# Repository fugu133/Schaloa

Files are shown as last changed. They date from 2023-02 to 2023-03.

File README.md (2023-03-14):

# 超小型分光光度計Schaloa
## 概要
浜松ホトニクスのマイクロ分光器[C12880MA](https://www.hamamatsu.com/jp/ja/product/optical-sensors/spectrometers/mini-spectrometer/C12880MA.html)を用いた分光光度計モジュールのハードウェア設計データです．  
本装置を使うと可視領域の分光計測や吸光光度分析がハンディサイズで実現可能です．  
主にCADはEagleとFusionを使用しています．詳しい仕様は[こちら](design_specifications.pdf)    

## 基板のイメージ
### メイン制御基板
分光器や各系の制御，PCとの通信を行います．



### 分光器基板
分光器のブレークアウト基板です．



## 計測デモ
蛍光灯と一般的な白色LEDの放射光スペクトルを計測しました．


### 蛍光灯
405nm，436nm，546nm及び577nm付近に鋭いピークが見られます．  
これらは蛍光灯の発光源である水銀の原子スペクトルと一致しています．  
この光を管内の蛍光体に照射すると蛍光により白色光が作成されます．

### 白色LED
頂点が過剰露出により潰れていますが，440nm付近に鋭いピークが見られます．  
これはパッケージ内部の青色LEDによる光だと考えられます．所謂ブルーライトです．  
また550nm-560nm付近を中心に広いピークを確認できます．  
これは黄色系の蛍光体の蛍光だと考えられます．白色LEDはこのようにして白色光を作成します．

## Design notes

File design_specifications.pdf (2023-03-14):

Kaiji Takeuchi 2019
[SCHLOA version beta]

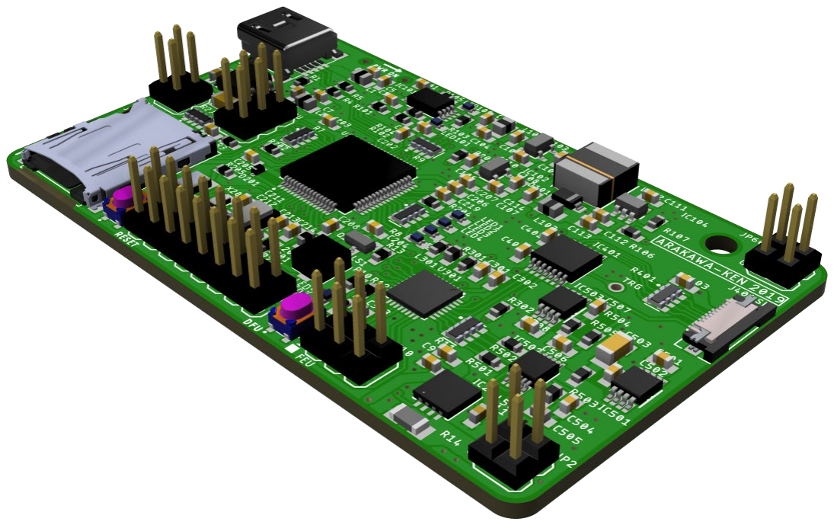
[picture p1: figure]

p. 1

# SCHLOA v1.0.0

Compact Portable Spectrophotometer | Developed by Kaiji Takeuchi 2019
1. 概要

SCHLOA (Fig.1.1) は分光分析法を採用した超小型ポータブル分光光度計です．コア・デ バイスである分光器には Hamamatsu Photonics 製ミニ分光器に対応しています．本システ

ムは持ち運べるサイズながら，反射，吸収，拡散及び散乱光の分光分析に対する，幅広い 応用が可能です．コア・システムには Arm® Mbed™を採用しているため，ファームウェア

開発も容易になります．

2. 特徴
・32 ビット Cortex-M4 コア・プロセッサ：STM32F446RE(180MHz)
・32 ビット Cortex-M4 デジタルフロントエンド・プロセッサ：STM32L432KC(80MHz) ・Arm® Mbed™ Mbed OS5 対応

・対応分光器波長感度
Hamamatsu Photonics MS series
-C11708MA：640nm～1050nm
-C10988MA-01：340nm～750nm
Hamamatsu Photonics micro series -C12880MA：340nm～780nm
-C12666MA：340nm～850nm
・蓄積(露出)時間：～100µs
・ADC キャプチャ・レート：～1MHz

・高精度・高速セトリング アナログフロントエンド
・ADC 専用リファレンス電源内臓
・LED ドライバ内臓
-PWM(電流フィードバック)

・リアルタイムクロック内臓
・各データ転送(記録)方式に対応
-Bluetooth SPP (専用基板が必要)
-USB I/F
-SD Memory Card

Fig. 1.1 SCHLOA Board

p. 2
3. 目次
1. 概要 | 1
2. 特徴 | 1
3. 目次 | 2
4. ブロック図と機能説明 | 5
■ メインボード | 5
5. ピンマップと機能説明 | 6
■ ピンマップ | 6
・Supply Port (JP1) | 6
・MPU Debug Port (JP601) | 6
・FEU Debug Port (JP602) | 6
・External Connection Port (JP603) | 7
・LED Output Port (JP2) | 7
・Spectrometer Connection Port (J401) | 7
・Auxiliary Port (JP604) | 7
■ 機能説明 | 8
6. 絶対定格 | 10
7. 推奨動作範囲 | 10
8. 内部回路とジャンクション | 11
■ 内部回路 | 11
・Main System | 11
・Power Unit | 12
・Main Processing Unit | 13
・Front End Processing Unit | 14
・Spectrometer Unit | 15
・A/D Convert Unit | 16
・Breakeout Pins (External Access Port) | 17
■ 内部ジャンクション | 18
9. 内部回路の動作と機能説明 | 20
■ パワーマルチプレクサの動作 | 20
・電源供給の切り替え | 20
・電流制限 | 20
■ リセット回路の動作 | 21
・パワーオン時のリセットシーケンス | 21
■ LED ドライバの動作 | 22
・出力電流の設定 | 22

p. 3
・輝度調整 | 22
・保護回路の動作 | 22
■ 音声出力機能 | 22
■ 分光器の蓄積 (露出) 動作 | 23
・タイミングチャート | 23
・推奨動作範囲 | 23
・最小蓄積 (露出) 時間の算出法 | 23
■ ビデオ信号のキャプチャ動作 | 24
・トリガ・モード | 24
・タイミングチャート | 25
・AD コンバータのリファレンス電源 | 26
■ メインコントロール・ユニットとデジタルフロントエンド・ユニットの通信 ........ 27
・タイミングチャート | 27
■ データフォーマット | 28
・Check Sum (XOR)の算出法 | 30
ファームウェア書き込みとシリアルデバッグ | 31
・DAP または Writer を使用する場合 | 31
・DFU Bootloader を使用する場合 | 31
10. ソフトウェアの機能説明 | 32
■ システムクロックの設定 | 32
・JSON を変更し HSE XTAL の使用を有効にする | 32
・クロック周辺の設定を自身で行い HSE XTAL の使用を有効にする | 33
■ MCO の設定 | 34
Mbed プラットフォームの変更箇所 | 35
・C++11 でプログラミングを行う | 35
・SPI 関係の API の改良 | 35
■ 専用 API (schloa-api) の概要 | 37
■ ADC API | 37
・ADC Class | 37
■ Backup API | 39
・Backup Class | 39
■ Communication API | 40
・CommunicationMaster Class | 40
・CommunicationSlave Class | 44
・MPUToFEUFitting Class | 47
・FEUToMPUFitting Class | 54

p. 4
・Fitting Class | 56
■ DebugPort API | 58
・DebugPort Class | 58
■ DrawSpectrum API | 59
・DrawSpectrum Class | 59
・DrawSpectrumAnalyze Class | 61
■ FastOut API | 63
・FastOut Class | 63
■ LEDDrive API | 65
・LEDDrive Class | 65
■ LiquidCrystal API | 67
・LiquidCrystal Class | 67
■ SoftPWMOut API | 69
・SoftPWMOut Class | 69
■ SystemTicker API | 72
・System Ticker Class | 72
■ Sound API | 75
・Sound Class | 75
■ Spectoro API | 77
・Spectro Class | 77
■ SwitchStatus API | 80
・SwitchStatus Class | 80
■ スペクトル表示アプリケーション drawSpectrum | 82
・データフォーマット | 83
・操作方法 | 85

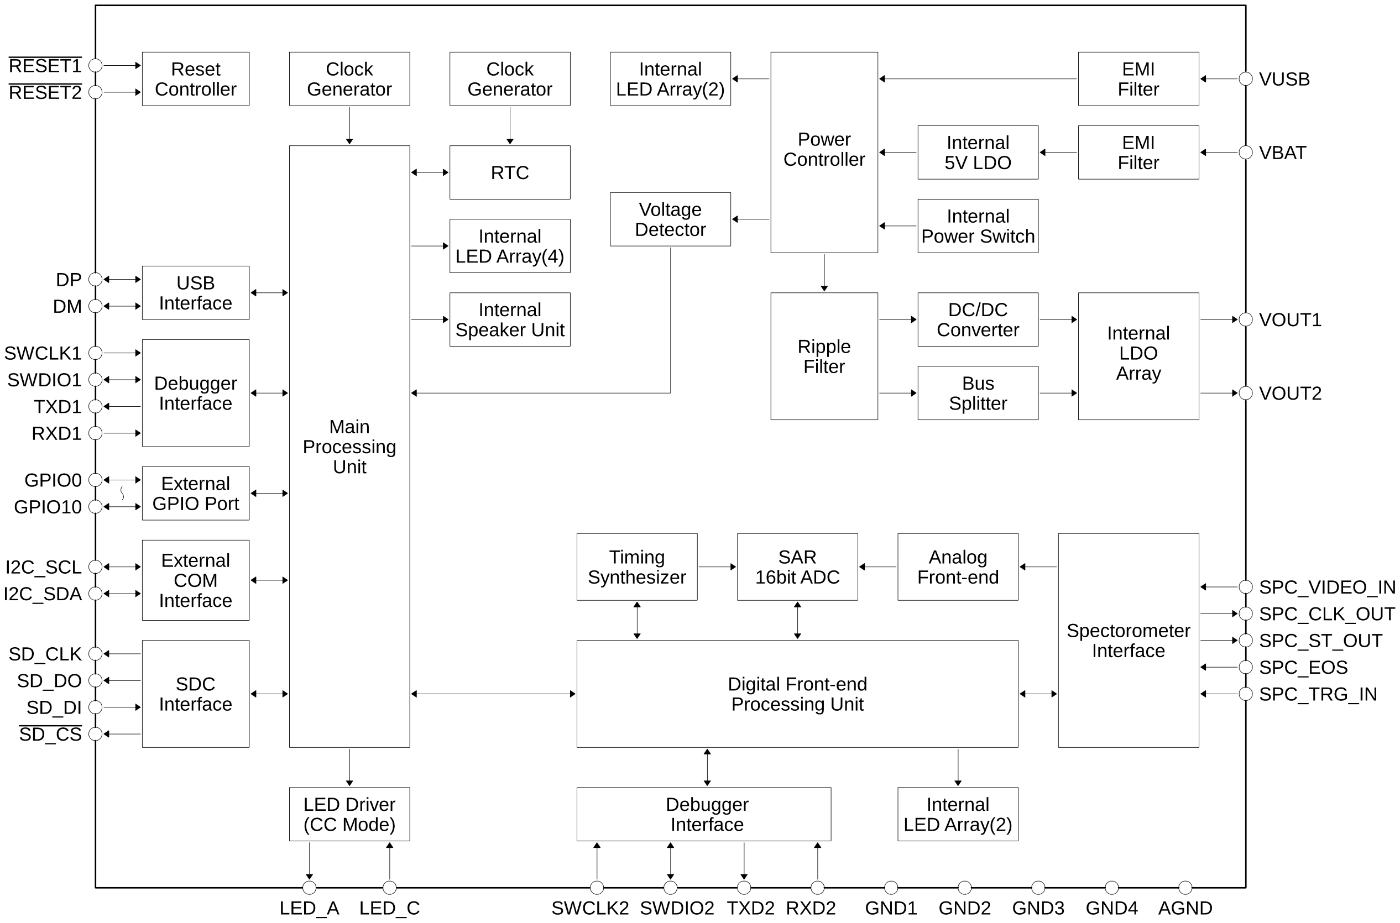
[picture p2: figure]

p. 5
4. ブロック図と機能説明

■ メインボード

Fig. 4.1 Main Board’s System Block Diagram

p. 6
5. ピンマップと機能説明

■ ピンマップ

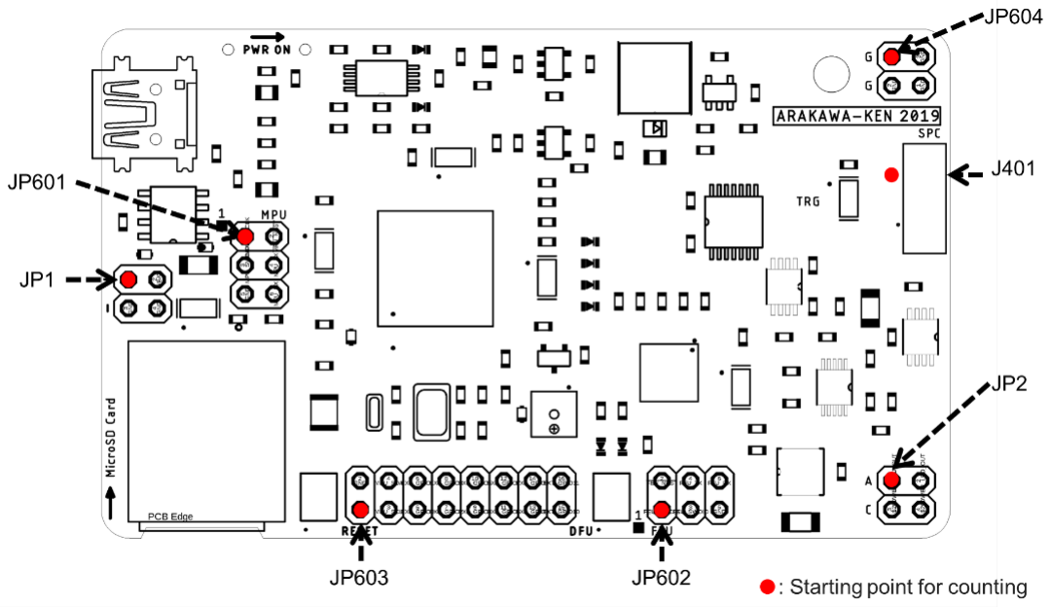
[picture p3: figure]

Fig. 5.1 Junction Ports Map

・Supply Port (JP1)

Fig. 5.2 JP1 Pins Map

・MPU Debug Port (JP601)

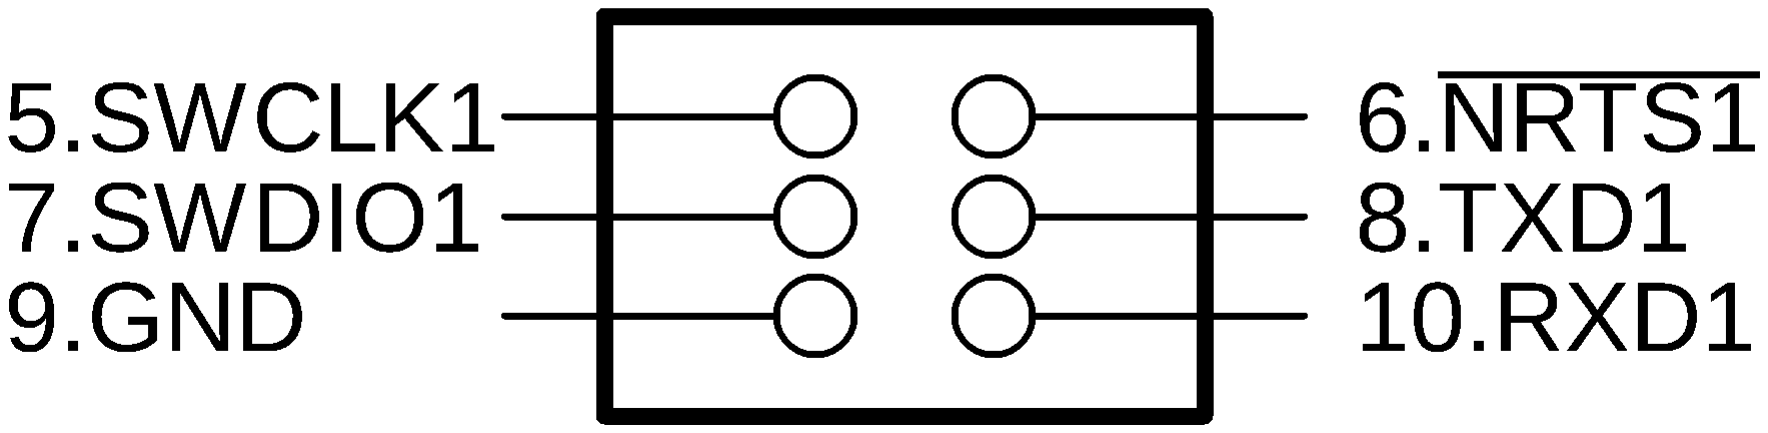
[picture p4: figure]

Fig. 5.3 JP601 Pins Map

・FEU Debug Port (JP602)

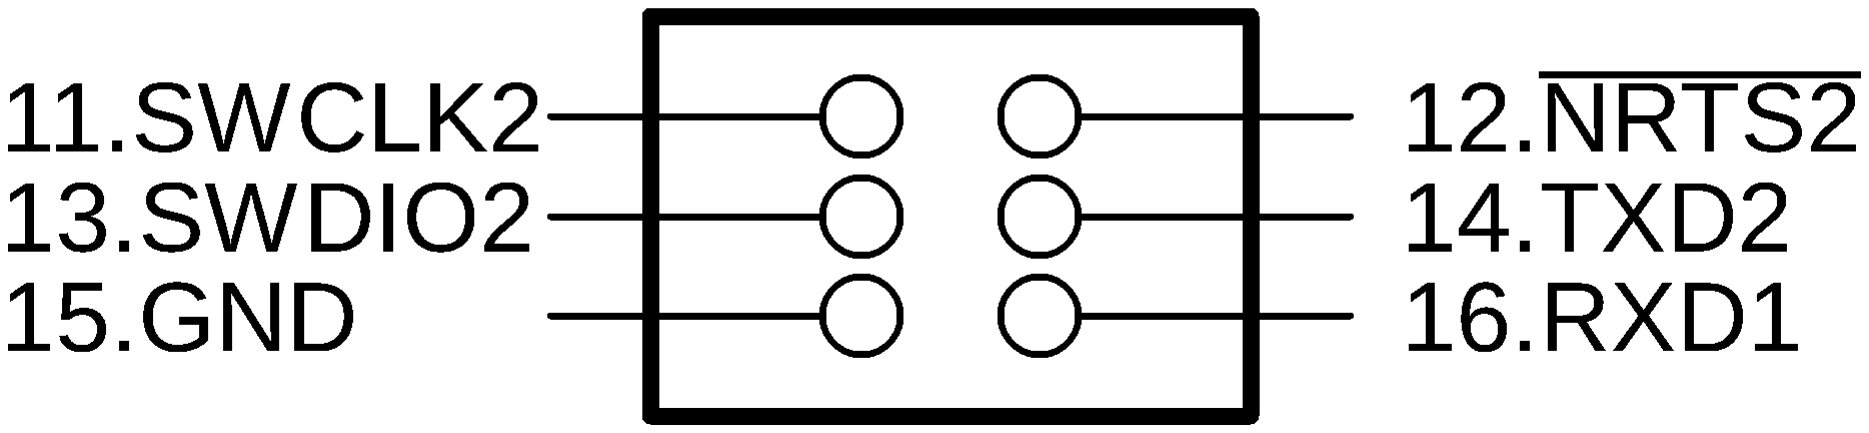
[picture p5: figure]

Fig. 5.4 JP602 Pins Map

p. 7

・External Connection Port (JP603)

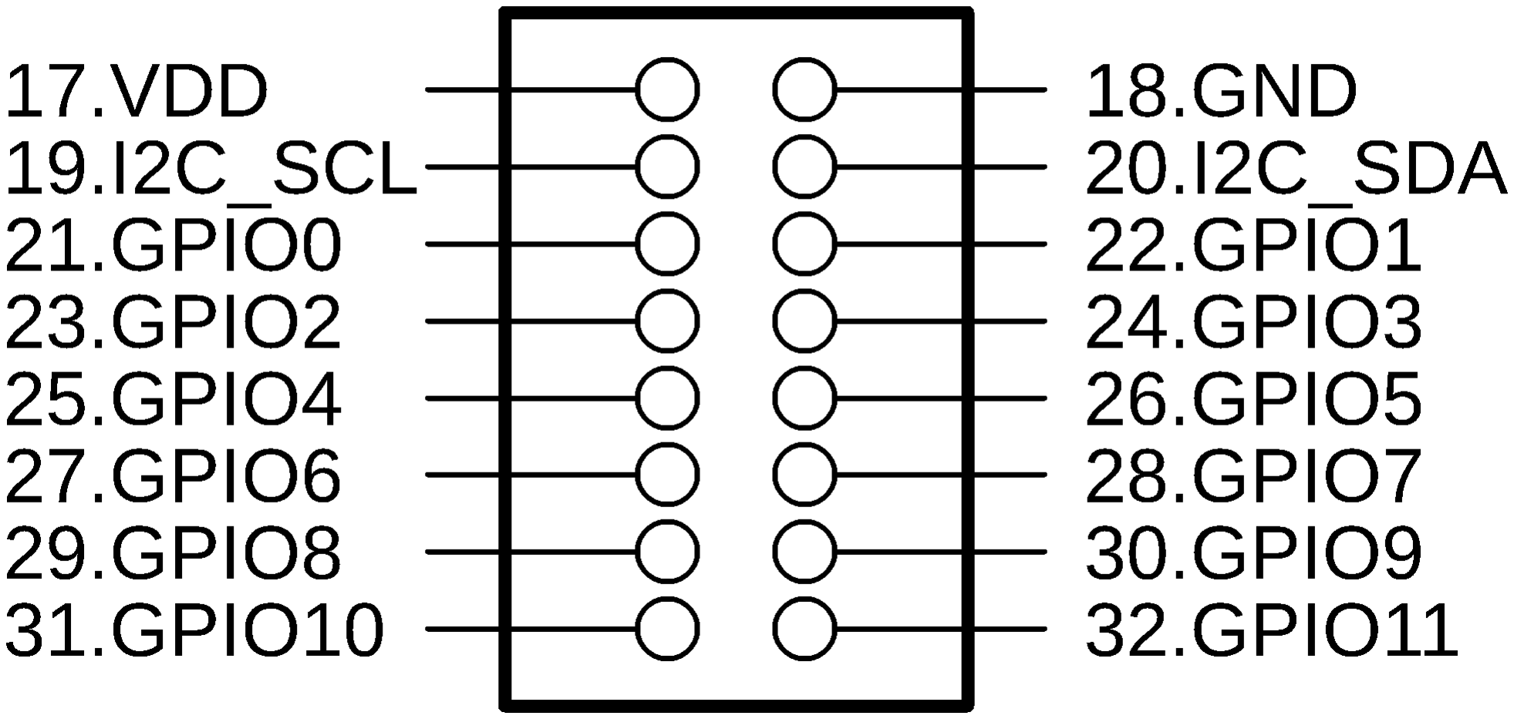
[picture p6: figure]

Fig. 5.5 JP603 Pins Map

・LED Output Port (JP2)

Fig. 5.6 JP2 Pins Map

・Spectrometer Connection Port (J401)

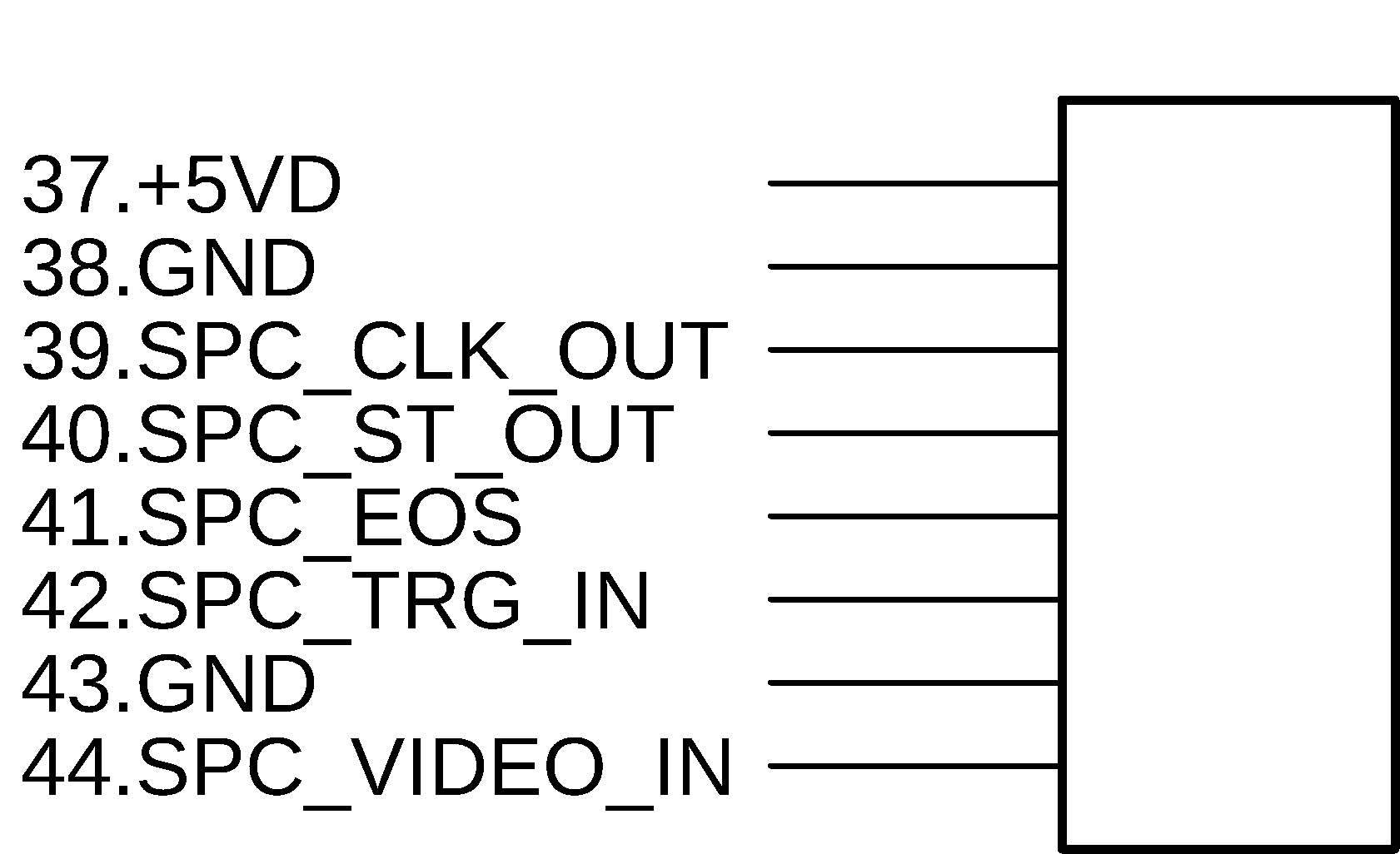
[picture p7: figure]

Fig. 5.7 J401 Pins Map

・Auxiliary Port (JP604)

Fig. 5.8 JP604 Pins Map

p. 8

■ 機能説明
Tabel 5.1 Pin Functions
NO. | Symbol | I/O | Tolerant | Function
1 | VBAT | - | - | Power Supply Pin, 5.1~10V
2 | VBAT | - | - | Power Supply Pin, 5.1~10V
3 | GND | - | - | Ground Pin
4 | GND | - | - | Ground Pin
5 | SWCLK1 | I | FT | MPU JTAG/SWD Clock Input Pin
6 | NRST1 | I | TT | MPU Reset Input Pin, Active Low
7 | SWDIO1 | I/O | FT | MPU JTAG/SWD Data I/O Pin
8 | TXD1 | O | FT | MPU UART Transmit Data Pin -Connect the RXD pin of the debugger.
9 | GND | - | - | Ground Pin
10 | RXD1 | I | FT | MPU UART Receive Data Pin -Connect the RXD pin of the debugger.
11 | SWCLK2 | I | FT | FEU JTAG/SWD Clock Input Pin -Connect the SWCLK pin of the debugger.
12 | NRST2 | I | TT | FEU Reset Input Pin, Active Low -Connect the Reset pin of the debugger.
13 | SWDIO2 | I/O | FT | FEU JTAG/SWD Data I/O Pin -Connect the SWDIO pin of the debugger.
14 | TXD2 | O | FT | FEU UART Transmit Data Pin -Connect the RXD pin of the debugger.
15 | GND | - | - | Ground Pin
16 | RXD2 | I | FT | FEU UART Receive Data Pin -Connect the RXD pin of the debugger
17 | +5VD | - | - | Digital Power Output Pin, +5V Constant
18 | GND | - | - | Ground Pin
19 | I2C_SCL~ | I/O | FT | I-squared-C Slave Clock Pin, Open Drain
20 | I2C_SDA~ | I/O | FT | I-squared-C Slave Data Pin, Open Drain
21 | EXT_GPIO0 | I/O | FT | External General-Purpose Input/Output Pin
22 | EXT_GPIO1 | I/O | FT | External General-Purpose Input/Output Pin -PWM is Available
23 | EXT_GPIO2 | I/O | FT | External General-Purpose Input/Output Pin -PWM is Available.

p. 9

Note1 : FT = 5V Input Tolerant，TT = 3.3V Input Tolerant.
Note2 : チルダ表記(~)された入出力ピンはオープン・ドレインです．
Note3 : アスタリスク表記(*)された入出力ピンは内部でプル・ダウンされています．
24 | EXT_GPIO3 | I/O | FT | External General-Purpose Input/Output Pin -PWM is Available.
25 | EXT_GPIO4 | I/O | FT | External General-Purpose Input/Output Pin -PWM is Available.
26 | EXT_GPIO5 | I/O | FT | External General-Purpose Input/Output Pin -PWM is Available.
27 | EXT_GPIO6 | I/O | FT | External General-Purpose Input/Output Pin
28 | EXT_GPIO7 | I/O | FT | External General-Purpose Input/Output Pin
29 | EXT_GPIO8 | I/O | FT | External General-Purpose Input/Output Pin
30 | EXT_GPIO9 | I/O | FT | External General-Purpose Input/Output Pin
31 | EXT_GPIO10 | I/O | FT | External General-Purpose Input/Output Pin
32 | EXT_GPIO11 | I/O | FT | External General-Purpose Input/Output Pin
33 | LED_A | O | - | Power LED Anode Pin, MAX 500mA
34 | LED_A | O | - | Power LED Anode Pin, MAX 500mA
35 | LED_C | I | - | Power LED Cathode Pin, Current FB
36 | LED_C | I | - | Power LED Cathode Pin, Current FB
37 | +5VD | - | - | Digital Power Output Pin, +5V Constant
38 | GND | - | - | Ground Pin
39 | SPC_CLK_OUT* | O | FT | Spectrometer Clock Output Pin -Mounting R502, Auto Trigger Mode. -Mounting R501, Manual Trigger Mode.
40 | SPC_ST_OUT* | O | FT | Spectrometer Start Pulse Output Pin
41 | SPC_EOS* | I | FT | Spectrometer End of Scan Detect Pin
42 | SPC_TRG_IN* | I | FT | Spectrometer Trigger Pulse Input Pin - No connection with controller
43 | GND | - | - | Ground Pin
44 | SPC_VIDEO_IN | I | - | Spectrometer Video Signal Input, 0~+5V
45 | GND | - | - | Ground Pin
46 | GND | - | - | Ground Pin
47 | GND | - | - | Ground Pin
48 | GND | - | - | Ground Pin

p. 10
6. 絶対定格
Tabel 6.1 Absolute Maximum Ratings Note：VSS = 0V
Parameter | min | max | Unit
VBAT | Battery Input Voltage | -0.3 | 10 | V
VUSB | USB Input Voltage | -0.3 | 5.0 | V
VCNT | Controller Input Voltage | -0.3 | 4.0 | V
Vxx-VSS | Delta Ground Voltage | -0.3 | - | V
VIOFT(PIN) | GPIO FT Pins input Voltage | VSS - 0.3 | VCNT + 4.0 | V
VIOTT(PIN) | GPIO TT Pins input Voltage | VSS - 0.3 | 4.0 | V
IIO(PIN) | GPIOs I/O Current | -25 | 25 | mA
∑IIO(PIN) | GPIOs Total I/O Current | -80 | 80 | mA
ILED | LED Driver Output Current | - | 600 | mA
TA | Operating Free-Air Temperature | 5 | 50 | ℃
Tstg | Storage Temperature | -20 | 70 | ℃
7. 推奨動作範囲
Tabel 7.1 Recommended Operating Condition Ranges
Parameter | min | typ | max | Unit
VBAT | Battery Input Voltage | 5.1 | 9.0 | 10 | V
VUSB | USB Input Voltage | 4.8 | 5.0 | 5.5 | V
VCNT | Controller Input Voltage | 3.0 | 3.3 | 4.0 | V
TA | Operating Free-Air Temperature | 5 | 20 | 40 | ℃

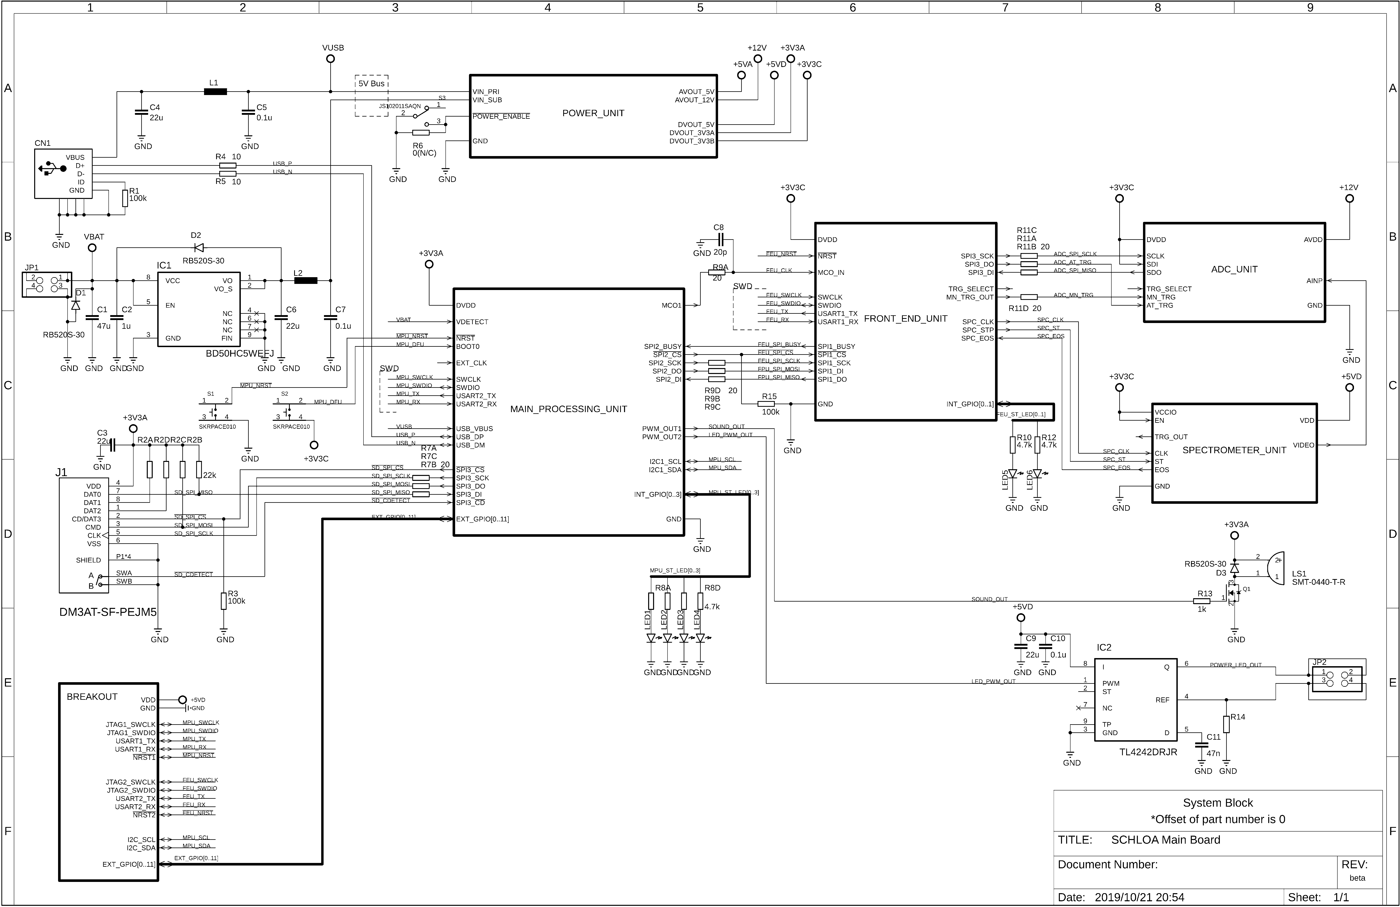
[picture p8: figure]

p. 11
8. 内部回路とジャンクション

■ 内部回路

ピンラベルやワイヤラベルに若干の差異がありますが，内部回路は次のようになっていま す．ユニット毎に，部品番号に 100 刻みのオフセットが加わります．

・Main System

Fig. 8.1 Main Schematic

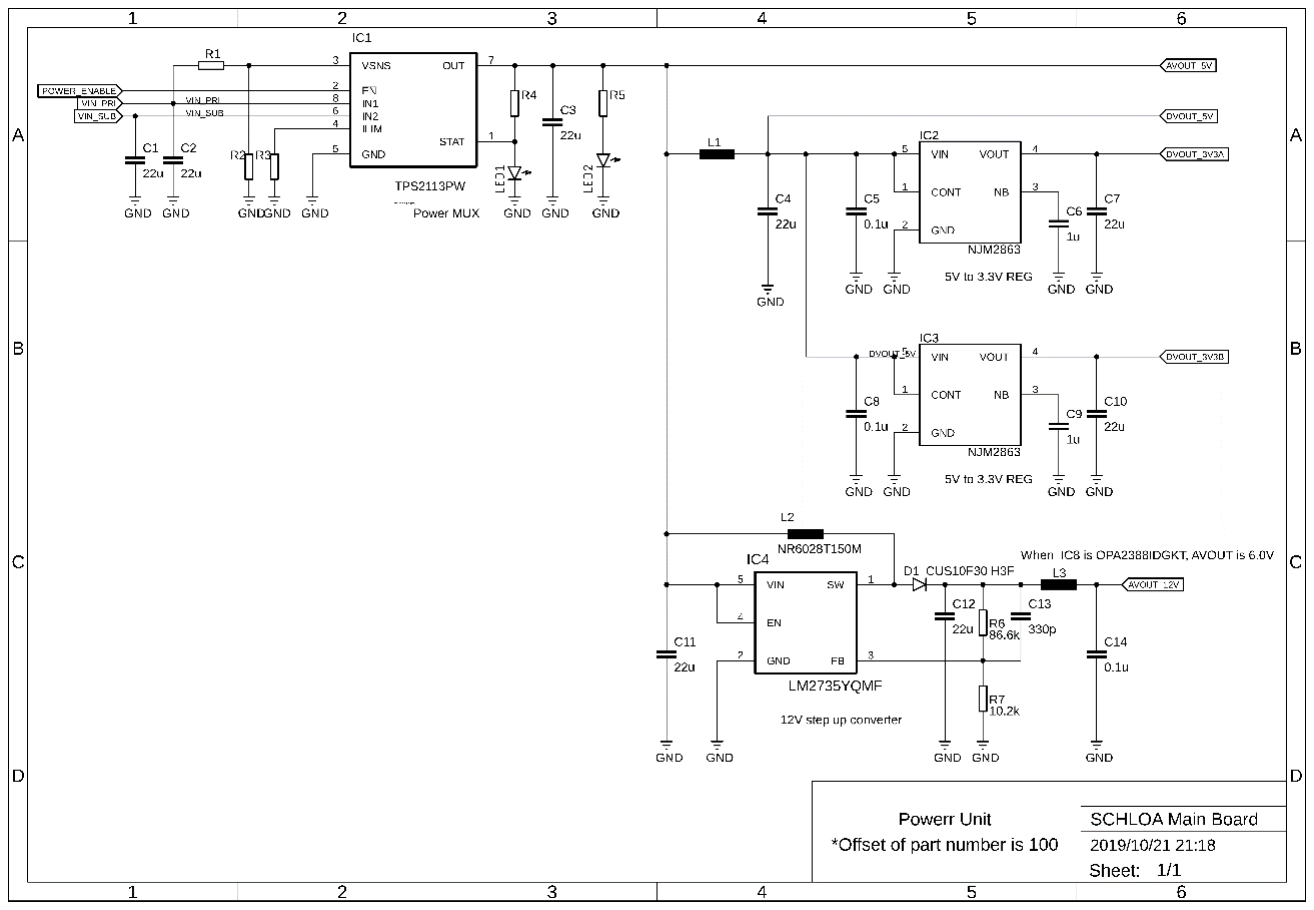
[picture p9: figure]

p. 12

・Power Unit

Fig. 8.2 Power Unit Schematic

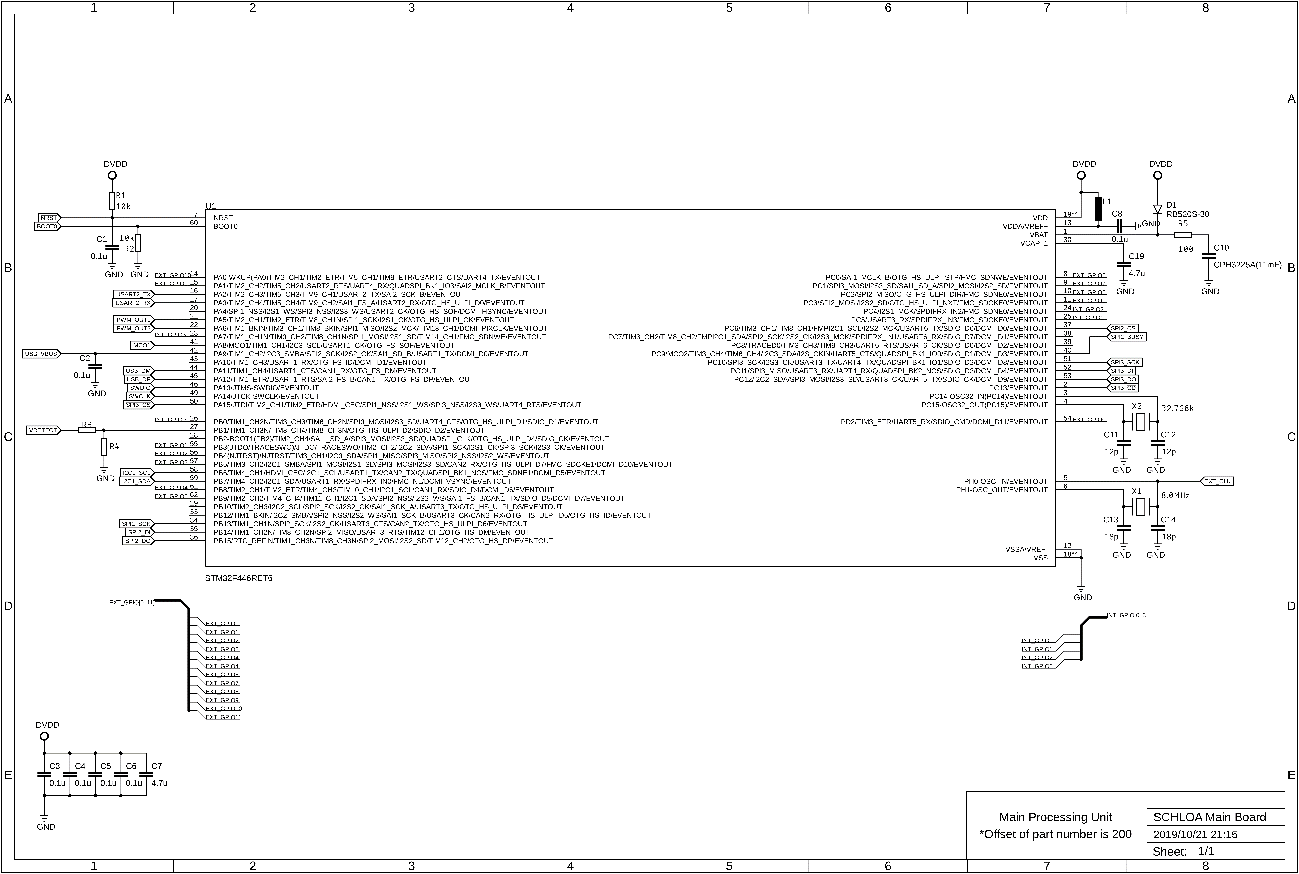
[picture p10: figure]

p. 13

・Main Processing Unit

Fig. 8.3 Main Processing Unit Schematic

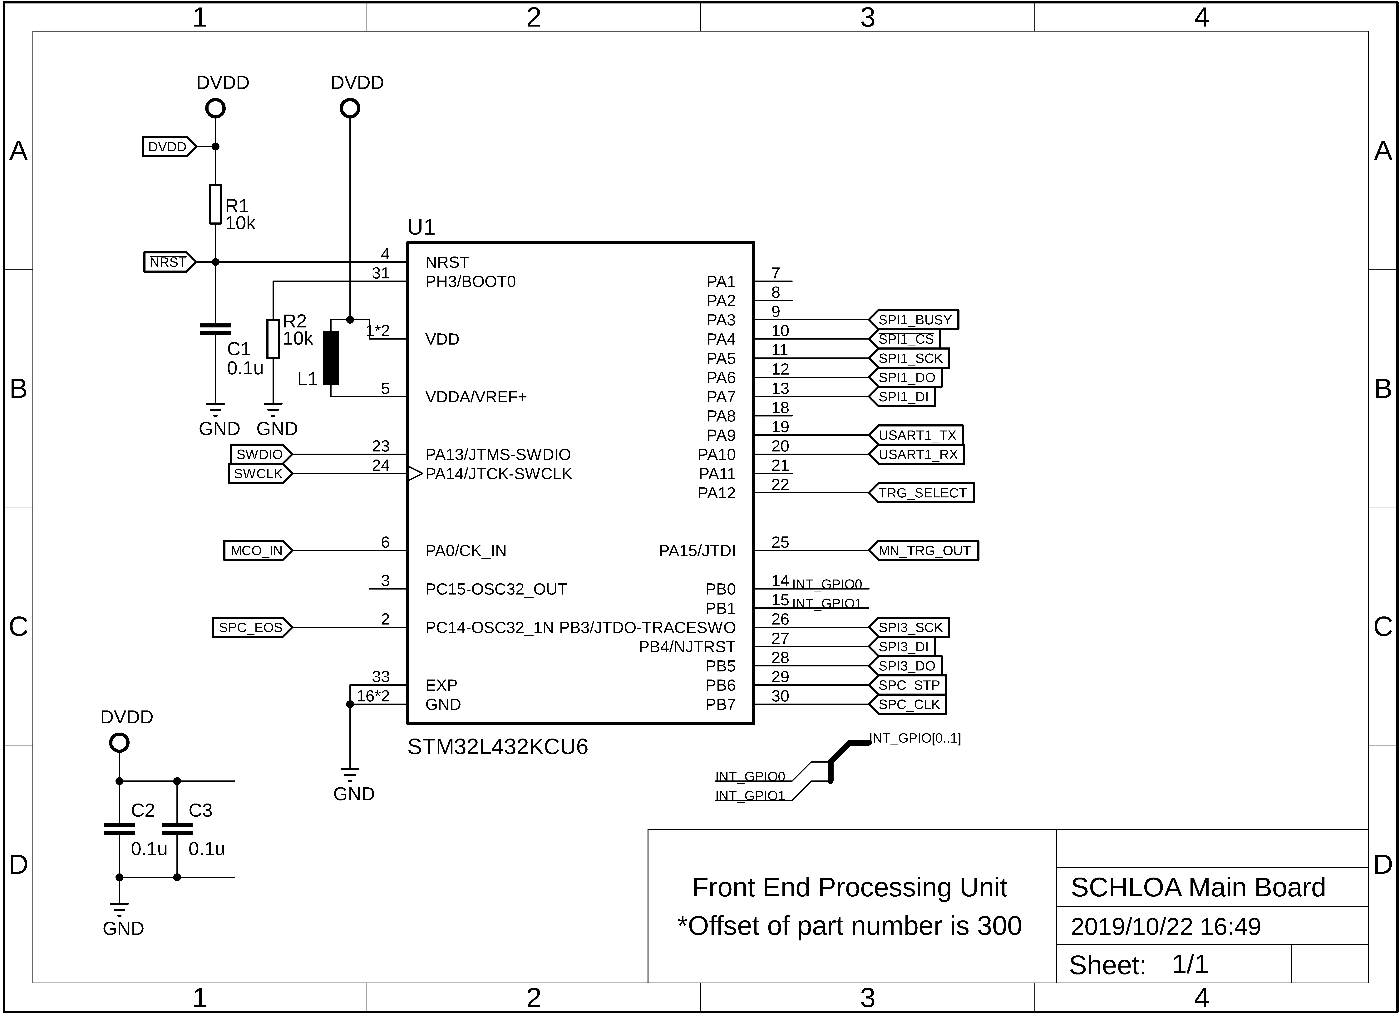
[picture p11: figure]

p. 14

・Front End Processing Unit

Fig. 8.4 Front End Processing Unit Schematic

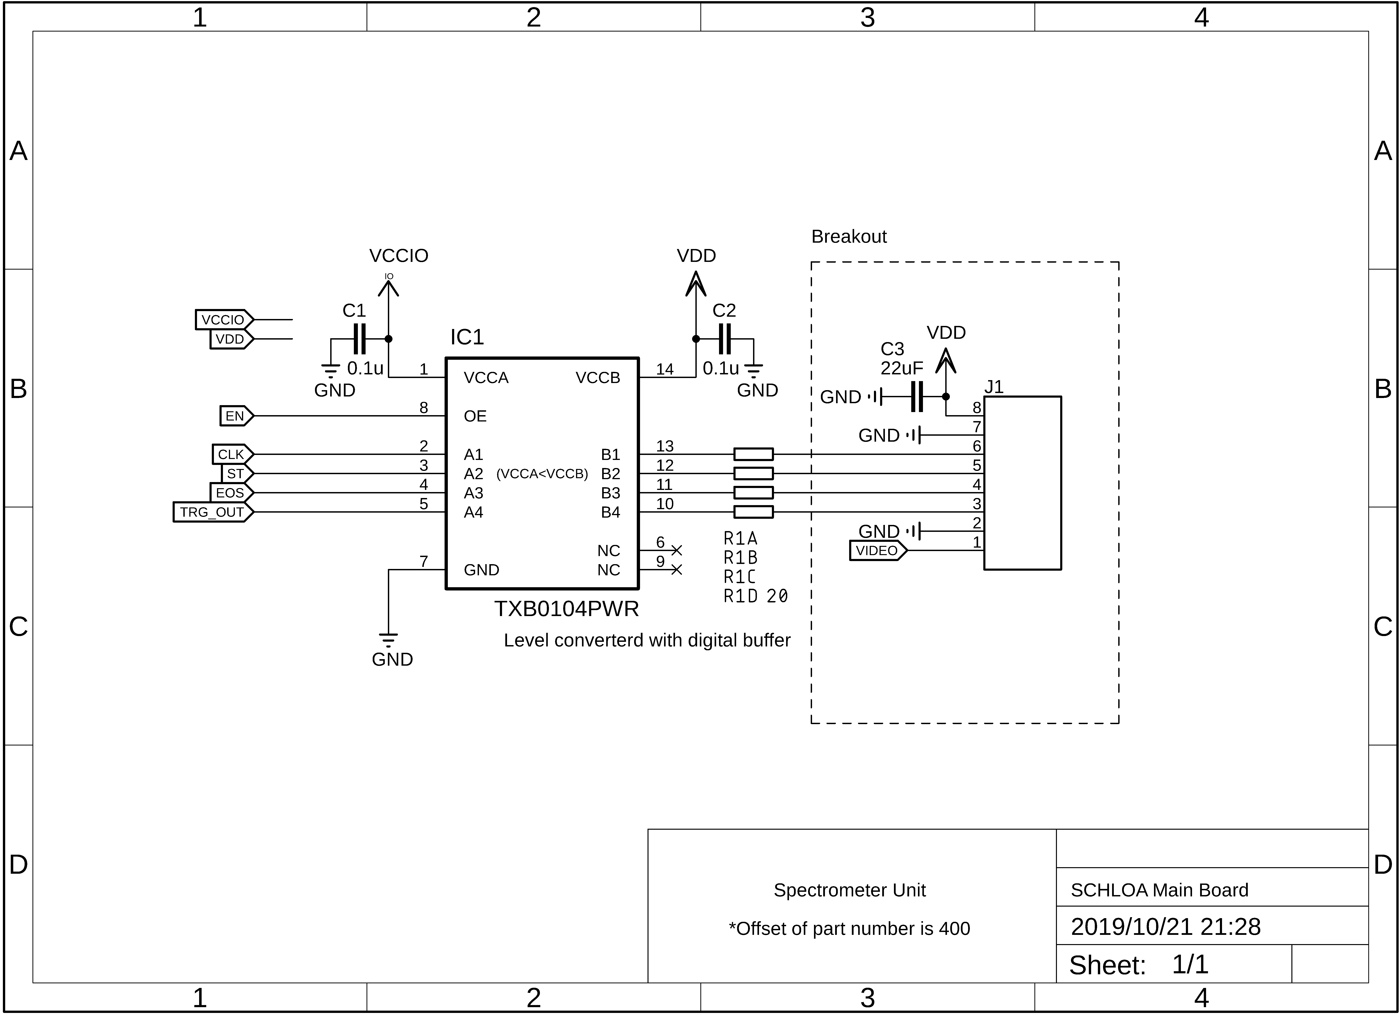
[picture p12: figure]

p. 15

・Spectrometer Unit

Fig. 8.6 Spectrometer Unit Schematic

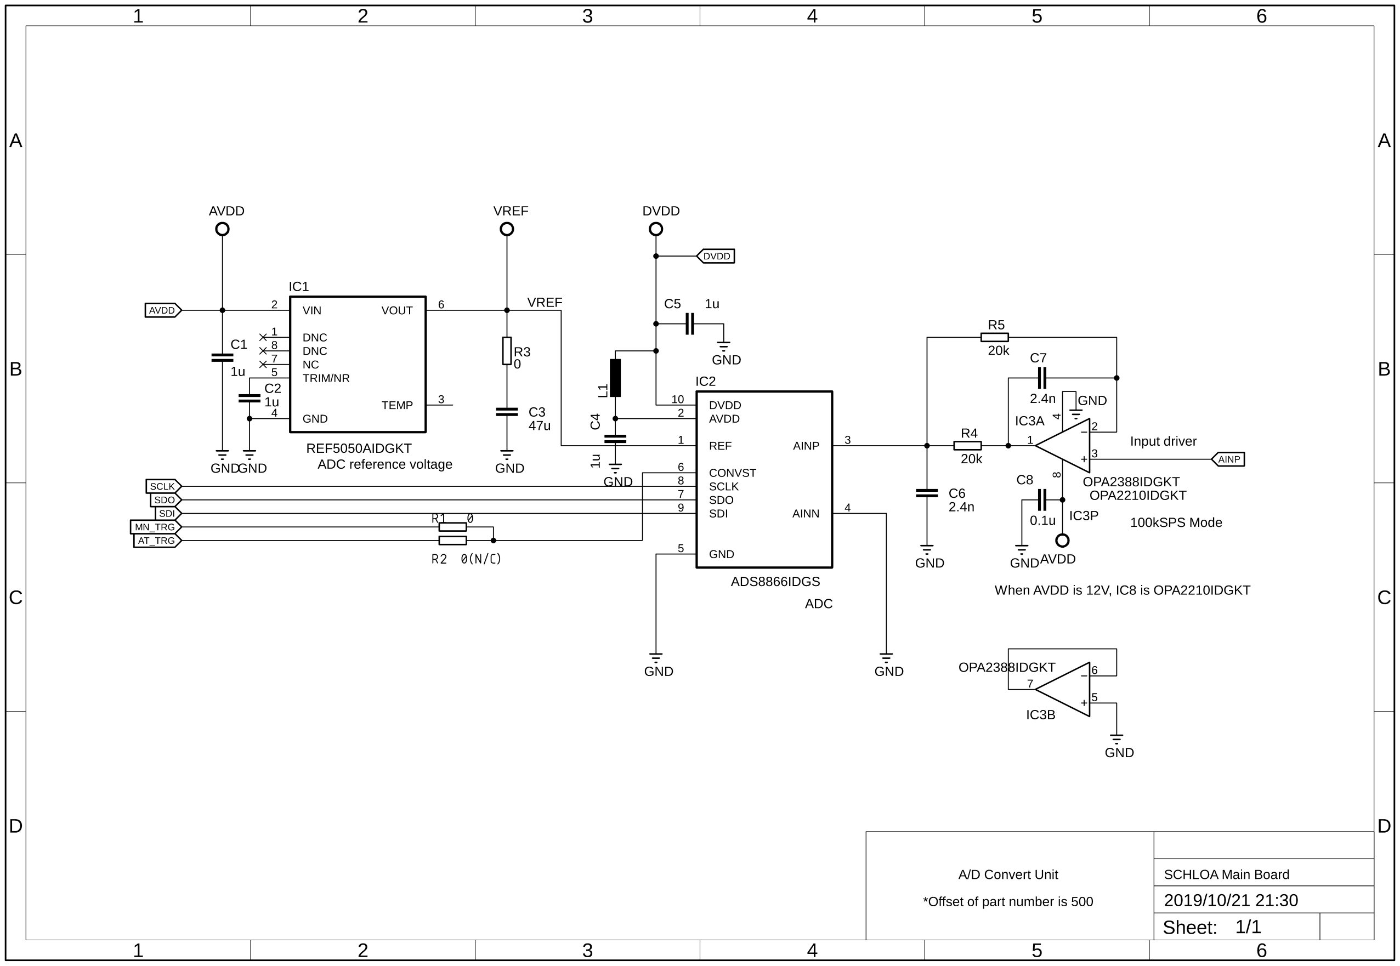
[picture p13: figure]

p. 16

・A/D Convert Unit

Fig. 8.7 A/D Convert Unit Schematic

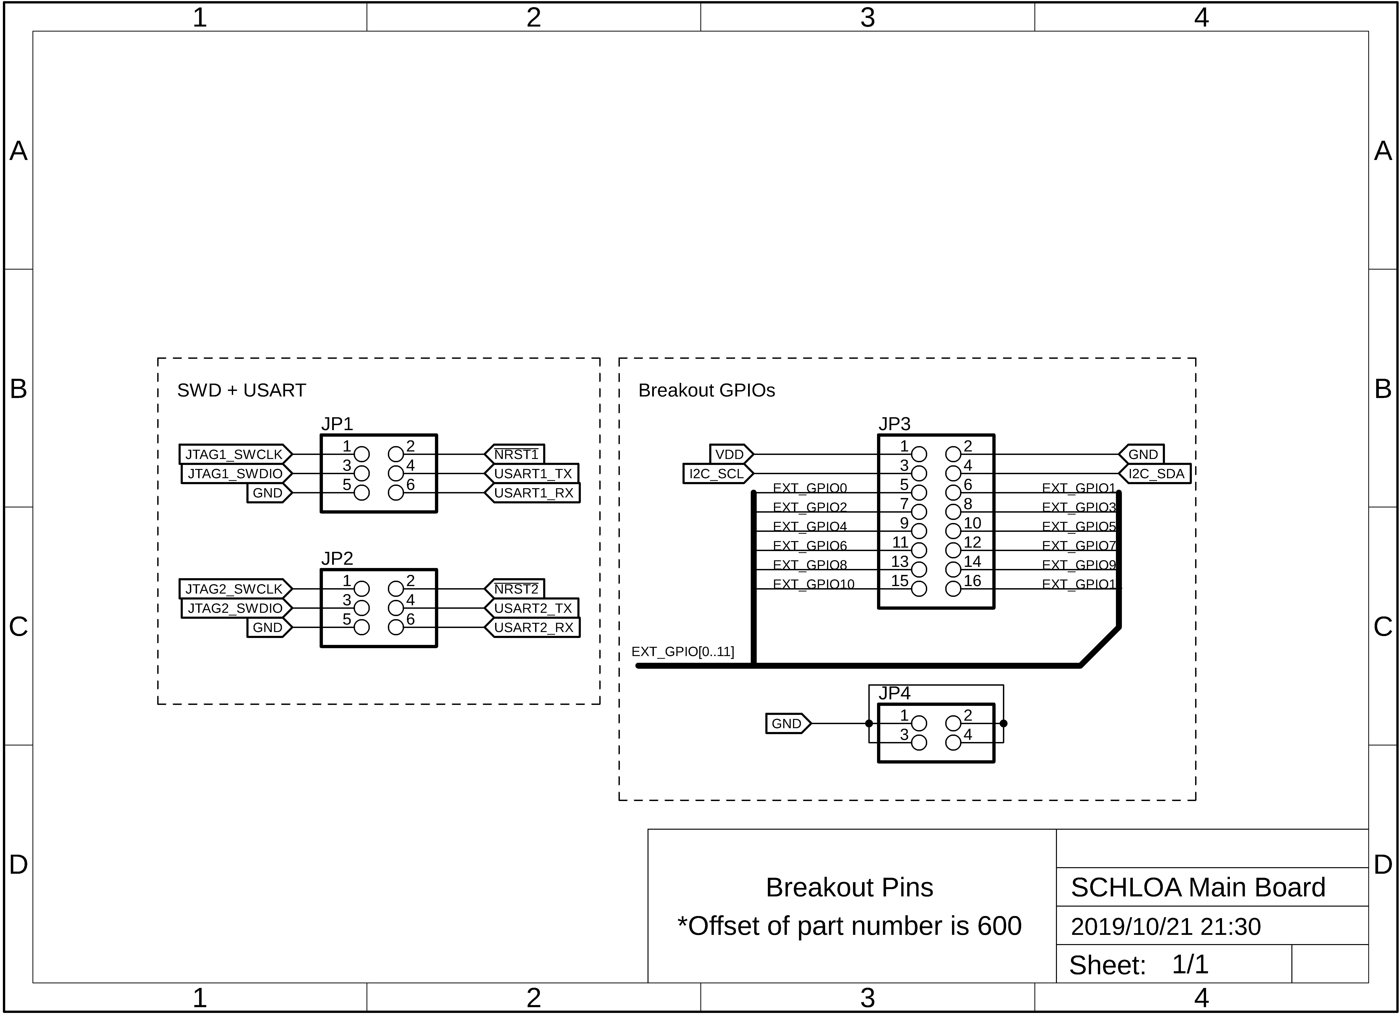
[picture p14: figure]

p. 17

・Breakeout Pins (External Access Port)

Fig. 8.8 Breakeout Pins Schematic

p. 18

■ 内部ジャンクション

■ Tabel 8.1 Internal Bus Junctions
Net Symbol | Net Function | Junction
From | To
VDETECT | Voltage Detect | STM32F446RE PB1 | Battery Power Bus
MPU_NRST# | Reset Signal Input | STM32F446RE NRST | S1, (6.NRST1)
MPU_DFU* | Boot Mode Select | STM32F446RE BOOT0 | S2
MPU_SWCLK | SWD Clock Input | STM32F446RE PA14 | (5.SWCLK1)
MPU_SWDIO | SWD Data I/O | STM32F446RE PA13 | (7.SWDIO1)
MPU_TX | USART TX | STM32F446RE PA2 | (8.TXD1)
MPU_RX | USART RX | STM32F446RE PA3 | (10.RXD1)
USB_VBUS | USB Bus Input | STM32F446RE PA9 | USB Power Bus
USB_DP | USB Data Pulse | STM32F446RE PA11 | USB Data Bus
USB_DM | USB Data Minus | STM32F446RE PA12 | USB Data Bus
SD_SPI_CS* | SDC SPI Select | STM32F446RE PC13 | SDC CD
SD_SPI_SCLK# | SDC SPI Clock | STM32F446RE PC10 | SDC CLK
SD_SPI_MOSI# | SDC SPI MOSI | STM32F446RE PC12 | SDC DI
SD_SPI_MISO# | SDC SPI MISO | STM32F446RE PC11 | SDC DO
EXT_GPIO0 | External GPIO | STM32F446RE PD2 | (21.GPIO0)
EXT_GPIO1 | External GPIO | STM32F446RE PB3 | (22.GPIO1)
EXT_GPIO2 | External GPIO | STM32F446RE PB4 | (23.GPIO2)
EXT_GPIO3 | External GPIO | STM32F446RE PB5 | (24.GPIO3)
EXT_GPIO4 | External GPIO | STM32F446RE PB8 | (25.GPIO4)
EXT_GPIO5 | External GPIO | STM32F446RE PB9 | (26.GPIO5)
EXT_GPIO6 | External GPIO | STM32F446RE PC0 | (27.GPIO6)
EXT_GPIO7 | External GPIO | STM32F446RE PC1 | (28.GPIO7)
EXT_GPIO8 | External GPIO | STM32F446RE PC2 | (29.GPIO8)
EXT_GPIO9 | External GPIO | STM32F446RE PC3 | (30.GPIO9)
EXT_GPIO10 | External GPIO | STM32F446RE PA0 | (31.GPIO10)
EXT_GPIO11 | External GPIO | STM32F446RE PA1 | (32.GPIO11)
MPU_ST_LED0 | Status LED | STM32F446RE PB0 | LED1
MPU_ST_LED1 | Status LED | STM32F446RE PC5 | LED2
MPU_ST_LED2 | Status LED | STM32F446RE PC4 | LED3
MPU_ST_LED3 | Status LED | STM32F446RE PA7 | LED4

p. 19
MPU_SCL~ | I2C Slave Clock | STM32F446RE PB6 | (19.I2C_SCL)
MPU_SDA~ | I2C Slave Data | STM32F446RE PB7 | (20.I2C_SDA)
SOUND_OUT | Sound | STM32F446RE PA5 | LS1
LED_PWM_OUT | LED Driver PWM | STM32F446RE PA6 | TL4242 PWM
FEU_SPI_BUSY | FEU SPI Busy | STM32F446RE PC9 | STM32L432KC PA3
EFU_SPI_CS* | FEU SPI Select | STM32F446RE PC6 | STM32L432KC PA4
FEU_SPI_SCLK | FEU SPI Clock | STM32F446RE PB13 | STM32L432KC PA5
FEU_SPI_MOSI | FEU SPI MOSI | STM32F446RE PB15 | STM32L432KC PA7
FEU_SPI_MISO | FEU SPI MISO | STM32F446RE PB14 | STM32L432KC PA6
FEU_MCLK | System Clock | STM32F446RE PA8 | STM32L432KC PA0
FEU_NRST# | Reset Signal Input | STM32L432KC NRST | (12.NRST2)
FEU_SWCLK | SWD Clock Input | STM32L432KC PA14 | (11.SWCLK2)
FEU_SWDIO | SWD Data I/O | STM32L432KC PA13 | (13.SWDIO2)
FEU_TX | USART TX | STM32L432KC PA9 | (14.TXD2)
FEU_RX | USART RX | STM32L432KC PA10 | (16.RXD2)
ADC_ AT_TRG | ADC Auto Trigger | STM32L432KC PB5 | ADS88xx CONVST
ADC _MN_TRG | ADC Manual Trigger | STM32L432KC PA15 | ADS88xx CONVST
ADC_SPI_SCLK | ADC SPI Clock | STM32L432KC PB3 | ADS88xx SCLK
ADC_SPI_MISO | ADC SPI MISO | STM32L432KC PB4 | ADS88xx SDO
SPC_SCLK* | SPC Shift Clock | STM32L432KC PB7 | (39.SPC_CLK_OUT)
SPC_ST* | SPC Start Pulse | STM32L432KC PB6 | (40.SPC_ST_OUT)
SPC_EOS* | SPC End of Scan | STM32L432KC PC14 | (41.SPC_EOS)
FEU_ST_LED0 | Status LED | STM32L432KC PB0 | LED5
FEU_ST_LED1 | Status LED | STM32L432KC PB1 | LED6

Note1 : チルダ(~) 表記されたネット・シンボルはオープン・ドレインです．
Note2 : アスタリスク(*) 表記されたネット・シンボル内部でプル・ダウンされています． Note3 : シャープ(#) 表記されたネット・シンボルは内部でプル・アップされています． Note4 : 小括弧で包まれた接続先は外部アクセスポートです．

p. 20
9. 内部回路の動作と機能説明

本項で説明する殆どは．専用の API を用いることで無視することができます．API は汎用性

が最大に考慮されているため，動作速度を意識したソフトウェア設計やより高効率化，良特 性化を試みる際には熟読する必要があります．

■ パワーマルチプレクサの動作
電源マネジメントとして TEXAS INSTRUMENTS Auto-Switching Power Mux TPS2113PWR を
実装しています．バッテリー使用時に USB ケーブルを接続し，PC あるいはスマートフォン と通信を行う際，自動的に電源供給を USB に変更します．

・電源供給の切り替え
パワーマルチプレクサは VSNS ピンに入力される電圧によって，USB 電源 (IN1 ピン) とバ ッテリー電源 (IN2 ピン) が切り替わります．IN2 選択時のみ STAT ピンに接続された LED101 が点灯します．閾値電圧は 0.8V です，また，EN ピンに接続されたスライドスイッ チ SW101 を ON にすると電源供給を開始し，LED102 が点灯します．入出力の真理値表は

次のようになります．

Tabel 9.1 Output Truth Table
SW101 | VI(VSNS) > 0.8V | VI(IN2) > VI(IN1) | LED101 | LED102 | OUT
ON | Yes | X | L | H | IN1
ON | No | No | L | H | IN1
ON | No | Yes | H | H | IN2
OFF | X | X | L | L | Hi-Z
Note1 : X = Don’t Carre, Hi-Z = High Impedance.

標準では USB 電源による供給が最優先されるようになっていますが，VI(IN2) と VI(IN1)との 比較によって供給元を選択したい場合は R101 を取り外してください．

・電流制限
最大出力電流は 1.25 A ですが，制限抵抗 RLIM (R103)を変更することで出力制限 ILIM [A]が変 更可能です．RLIMは以下の式で決定されます．

# RLIM = 500

### ILIM

[Ω]

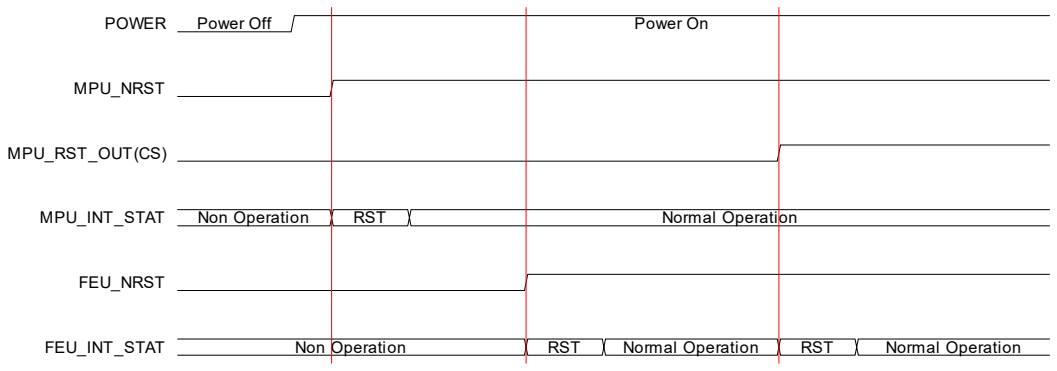
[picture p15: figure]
POWER; Power Off; Power On; MPU_NRST; MPU_RST_OUT(CS); MPU_INT_STAT; Non Operation; RST; Normal Operation; FEU_NRST; FEU_INT_STAT

p. 21

■ リセット回路の動作

・パワーオン時のリセットシーケンス

Fig. 9.1 Reset Sequence

各ユニットの NRST ピンはリセットシグナルを送らない限りはリセットされませんが，パ ワーオン時に限ってはその動作が異なります．NRST ピンには RC 回路による遅延回路が接 続されており，パワーオン時の立ち上がりタイミングが遅延します．Fig. 9.2 にリセット回

路の模式図を示します．

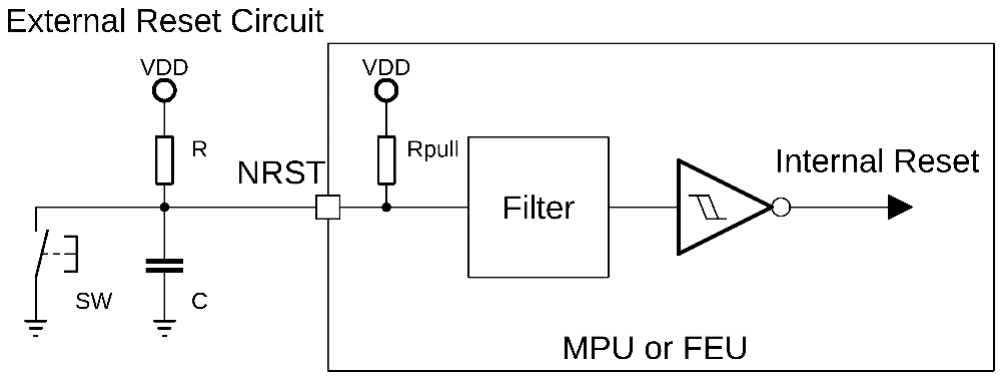
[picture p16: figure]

Fig. 9.2 Reset Circuit
NRST ピンのハイレベル・スレッショルド電圧VTHは 2V であり，パワーオンから内部リセ ット信号が発生するまでの遅延時間tdは次の式で算出できます．

# ttdd = CCCC pppppppp

+ pp

# llll VVDDDD

# VVDDDD − VVTTTT

[s]

ただし，R を実装しない場合は次のようになります．ただし，内部抵抗Rpullは 40 kΩです．

# ttdd = CC pppppppp llll VVDDDD VVDDDD − VVTTTT

[s]

また，FEU は転送データの CONF Byte の 4 bit 目に 1 セットし，MPU から転送することで リセットします．詳しくは Tabel 9.5 を参照してください．

p. 22

■ LED ドライバの動作
パワーLED ドライバとして，CC(Constant Current) Mode で動作する TEXAS INSTRUMENTS
LED Driver TL4242 を実装しています．最大 500 mA での定電流ドライブが可能です．複数 の LED を制御したい場合は専用のシールド基板を使用してください．

・出力電流の設定
リファレンス抵抗 RREF (R14)を変更することで出力電流 IQ [mA]を変更することができます． RREFは以下の式で決定されます．

# RRRRRRR = VVRRRRRR

IIQQ

[Ω]

VVRRRRRRは 0.177 mV と一定であり，RREF は 0.39～10 Ωであることが求められます．例えばを R14 に 0.39Ωを実装した場合の IQは 454 mA になります．

・輝度調整
PWM 信号を入力することで輝度調整を行えます．PWM 信号の High 時間のみドライバが動 作します．外部コンデンサ CD(C11) [F]を実装したときの，立下り遅延時間 TSTH(LOW) [ms]は

CCDDに比例し，次の式で決定されます．

# TTSS (LLLLLL) = CCDD

CCIIII

× 10 [ms]

CINTは 47 nF です．

・保護回路の動作
出力が開放及び短絡された際，極性を逆に接続した際，ドライバがオーバーヒートした際に

保護回路が働き ST ピンの出力が Low に設定されます．この時の出力遷移時間はTTSS (LLLLLL)

になります．

■ 音声出力機能
音声トランスデューサーとして PUI Audio Transducers SMT-0440-T-R を実装しています．メ
インコントロール・ユニットの PWM 出力ピンから信号を入力し，Nch MOS で構成された ローサイド・ドライバを介して出力します．共振周波数は 4000 ±500 Hz です．十分な音圧

を得たい場合，この帯域での使用が推奨されます．矩形波以外の音声出力を行いたい場合は PWM 方式あるいは PDM 方式で音声を変調してください．変調周波数が可聴域のため，場 合によっては RC ローパスフィルタを実装してください．

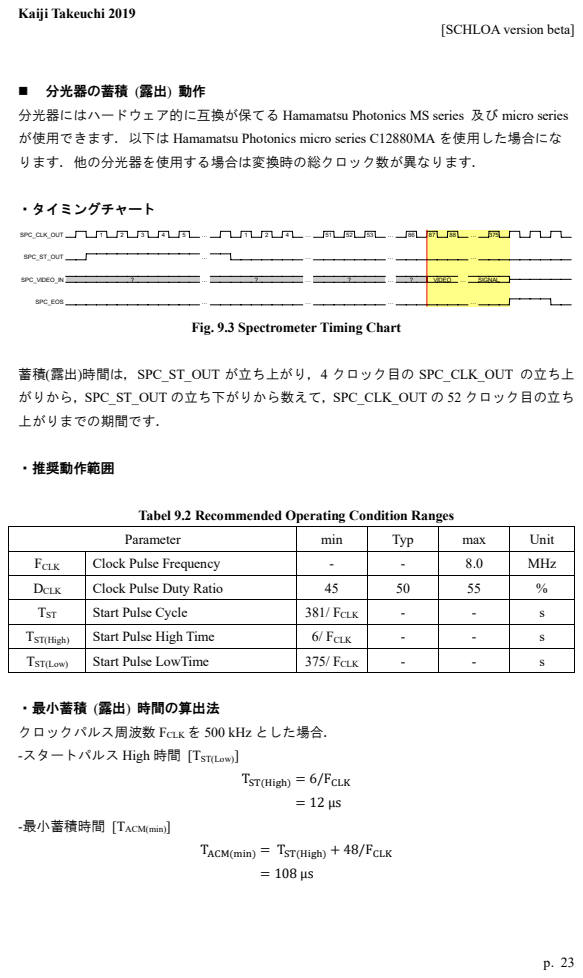
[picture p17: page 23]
・タイミングチャート; ・推奨動作範囲; SPC_CLK_OUT; SPC_ST_OUT; SPC_VIDEO_IN; VIDEO …; SIGNAL; SPC_EOS

■ 分光器の蓄積 (露出) 動作
分光器にはハードウェア的に互換が保てる Hamamatsu Photonics MS series 及び micro series
が使用できます．以下は Hamamatsu Photonics micro series C12880MA を使用した場合にな
ります．他の分光器を使用する場合は変換時の総クロック数が異なります．

Fig. 9.3 Spectrometer Timing Chart

蓄積(露出)時間は，SPC_ST_OUT が立ち上がり，4 クロック目の SPC_CLK_OUT の立ち上
がりから，SPC_ST_OUT の立ち下がりから数えて，SPC_CLK_OUT の 52 クロック目の立ち
上がりまでの期間です．

Tabel 9.2 Recommended Operating Condition Ranges

Parameter | min | Typ | max | Unit

FCLK | Clock Pulse Frequency | - | - | 8.0 | MHz
DCLK | Clock Pulse Duty Ratio | 45 | 50 | 55 | %
TST | Start Pulse Cycle | 381/ FCLK | - | - | s
TST(High) | Start Pulse High Time | 6/ FCLK | - | - | s
TST(Low) | Start Pulse LowTime | 375/ FCLK | - | - | s

・最小蓄積 (露出) 時間の算出法
クロックパルス周波数 FCLKを 500 kHz とした場合．
-スタートパルス High 時間 [TST(Low)]

TST(High) = 6/FCLK
TACM(min) = TST(High) + 48/FCLK

-最小蓄積時間 [TACM(min)]

p. 24

■ ビデオ信号のキャプチャ動作
ビデオ信号のキャプチャには TEXAS INSTRUMENTS microPOWERTM ADS886x family に対

応しています，

Tabel 9.2 Compatible Devices
Thoroughput | Device Names | Digikey PN
100kSPS | ADS8866IDGSR | 296-39885-1-ND
400kSPS | ADS8864IDGSR | 296-39881-1-ND
680kSPS | ADS8862IDGSR | 296-39877-1-ND
1MSPS | ADS8860IDGSR | 296-50909-1-ND

本ボードでは低消費電力化のため，AD コンバータのキャプチャ・レートを 100 µs に設定し

ています．キャプチャ・レートを変更する場合，あるいは低歪み化する場合はフロントエン ド回路の RC キックバック・フィルタ回路を変更する必要があります．AD コンバータの入

力信号はステップ信号であるため，設計はそれほど難しくありません．入力信号の周波数は キャプチャ・レートと等しくなります．

・トリガ・モード
変換開始トリガの作成モードは，SPI ペリフェラルを用いてハードウェア的にトリガ信号を

作成するオートトリガ・モードとソフトウェア的にトリガ信号を作成するマニュアルトリ ガ・モードの 2 つがあります．どちらのモードを使用するにしても，フロントエンド・アン プの RC キックバック・フィルタ回路の帯域を考慮する必要がります．

-オートトリガ・モード
オートトリガ・モードはデジタルフロントエンド・ユニットの SPI ペリフェラルを利用し，

トリガ信号を作成するトリガ・モードです．変換時間は自由に変更できませんが，キャプチ ャ時に自動的にトリガを作成するため，スムーズに変換結果を読み込むことができます． このモードを有効にするには R502 を実装し，R501 を取り外す必要があります．

-マニュアルトリガ・モード
マニュアルトリガ・モードはデジタルフロントエンド・ユニットの GPIO ペリフェラルを利

用し，任意のタイミングでトリガ信号を作成させるトリガ・モードです．任意のタイミング でトリガを作成することができ，変換時間を自由に設定できる反面，読み込みのタイミング を考慮してトリガを作成する必要があります．
このモードを有効にするには R501 を実装し，R502 を取り外す必要があります．

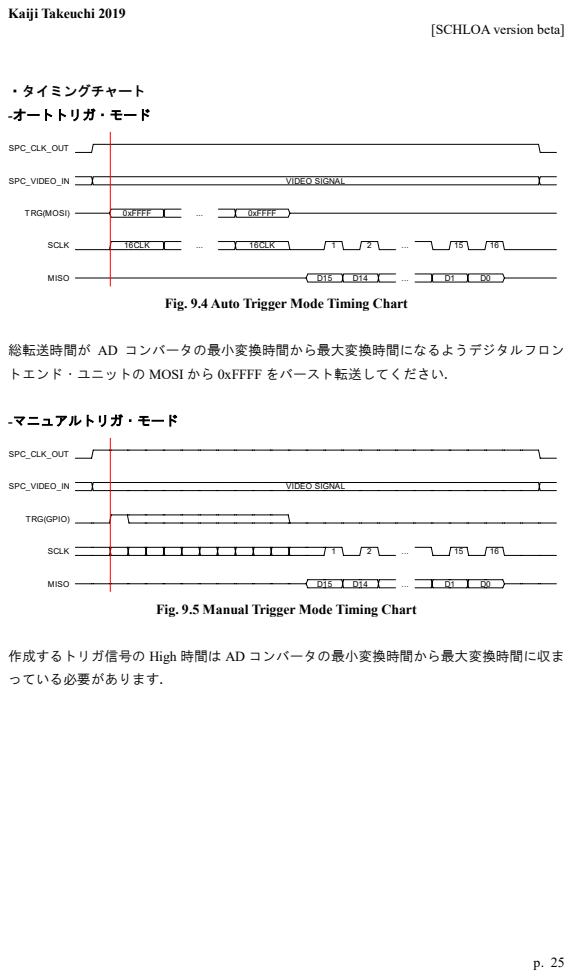
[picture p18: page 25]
・タイミングチャート; -オートトリガ・モード; -マニュアルトリガ・モード; SPC_CLK_OUT; SPC_VIDEO_IN; VIDEO SIGNAL; TRG(MOSI); 0xFFFF; SCLK; 16CLK; MISO; TRG(GPIO)

Fig. 9.4 Auto Trigger Mode Timing Chart

総転送時間が AD コンバータの最小変換時間から最大変換時間になるようデジタルフロン
トエンド・ユニットの MOSI から 0xFFFF をバースト転送してください．

Fig. 9.5 Manual Trigger Mode Timing Chart

作成するトリガ信号の High 時間は AD コンバータの最小変換時間から最大変換時間に収ま
っている必要があります．

p. 26

・AD コンバータのリファレンス電源
AD コンバータの基準電圧源には TEXAS INSTRUMENTS REF50xx に対応しています．分
光器のビデオ信号のピーク値が 5.0V であるため，REF5050 を標準で実装していますが，

基準電圧を変更したい場合には以下のデバイスを利用することができます．グレードによ り許容誤差，温度係数，ノイズが異なります．

Tabel 9.3 Compatible Devices
Output Voltage | Device Names | Digikey PN
1.0V | REF5010 | -
2.0V | REF5020 | -
2.5V | REF5025 | -
3.0V | REF5030 | -
4.0V | REF5040 | -
4.5V | REF5045 | -
5.0V | REF5050 | -

p. 27

■ メインコントロール・ユニットとデジタルフロントエンド・ユニットの通信 マスターである MPU とスレーブである FEU は 4-wire SPI + Busy 検出で通信を行います．

・タイミングチャート

Fig. 9.6 4-wire SPI Communication Timing Chart

FEU が蓄積(露出)を行っている際，あるいは ADC 読み込みを行っている際 (BUSY 状態) は SPI 通信に対する応答が無効になります．FEU がフリーな状態では BUSY ピンの出力が Low になり，SPI 通信が有効になります．但し，DMA を使う際にはその限りではありません． SPI の動作モードはモード 0 (正極パルス，立ち上がりラッチ，立下りシフト) ，MSB First です．転送バイトオーダは基本リトルエンディアンで行い，データブロック長は 578 Byte で

す．

ADC | | | | | | | | | | | ...
BUSY | | | | | | | | | | | ...
CS | | | | | | | | | | | ...
SCLK | | | | | | | | | | | ...
MOSI | ? | 7 | 6 | 5 | 4 | 3 | 2 | 1 | 0 | ? | 7 ... | ?
MISO | 7 | 6 | 5 | 4 | 3 | 2 | 1 | 0 | ... 1 | 0

p. 28

■ データフォーマット
-MPU→FEU の場合

データフォーマットは以下の様になります．
Tabel 9.4 MPU to FEU Transmit Data Formats
Byte | B0 | B1 | B2 | B4 | B5 | B6 | … | B576 | B577
Data | CONF | ACM_TIME[3…0] | | | | 0x00 | … | 0x00 | CSUM

CONF : Config Byte

Tabel 9.5 CONF Byte Data Formats
Bit | D7 | D6 | D5 | D4 | D3 | D2 | D1 | D0
Data | AEN | DEN | AMOD | RST | AVERAGEN[3…0]
Default | 0 | 0 | 0 | 0 | 0 | 0 | 0 | 0

AEN : Accumulation Enable
0 : Disable (default)
1 : Enable

DEN : Dark Correction Enable 0 : Disable (default)
1 : Enable

AMOD : Accumulation Mode
0 : Oneshot Mode (default)
1 : Continuous Mode

RST：FEU Reset
0 : Normal Operation (default) 1 : Reset

p. 29

AVERAGEN[3…0] : Average Number (MSB Fisrt)

# pixel_dataii = 1 NN pixel_dataii,jj

jj = 1

0b0000 : N = 1 (default, NonAverage)
0b0001 : N = 2 ~ 0b111 : N = 9 ~ 0b1111 : N = 17

ACM_TIME[3…0] : Accumulation Time [µs] (32bit unsigned integer) 例) ACM_TIME = 114514 µs
ACM_TIME を 10 進数から 16 進数に変換する．

# ACM_TIME = (114514)10 = (44417A9F)16

バイトオーダをビッグエンディアンにする．
0x44 | 0x41 | 0x7A | 0x9F

C_SUM : Check Sum (XOR)

-MPU←FEU の場合

Tabel 9.6 FEU to MPU Transmit Data Formats
Byte | B0 | B1 | … | B575 | B576 | B577
Data | PIX_DATA1[0…1] | | … | PIX_DATA288[0…1] | | CSUM

PIX_DATAx[0…1] : ADC Code for x th Pixel (16bit unsigned integer)
例) PIX_DATA16 = 810
PIX_DATA16 を 10 進数から 16 進数に変換する．

# PIX_DATA16 = (810)10 = (32A)16

バイトオーダをリトルエンディアンにする．
0x2A | 0x03

C_SUM : Check Sum (XOR)

p. 30

・Check Sum (XOR)の算出法
送信データブロック長を N としたとき，1 Byte のデータ並びを dT1, dT1, … , dTN とすると

Check Sum STCH(N) は 8bit の排他的論理和(XOR)による総和で表されます．

# STCH(N) = dT1⨁ dT2⨁ ⋯ ⨁ dTN

送信の際，STCH(N)をデータブロックの末尾に付加します．受信の際，受信データdR1, dR2, ⋯ , dRN と末尾の STCH(N)との Check Sum SRCH(N + 1)を計算します．

# SRCH(N + 1) = dR1⨁ dR2⨁ ⋯ ⨁ dRN ⨁ STCH(N)

この時，正常に送受信が行われていれば，受信データのみの Check Sum とSTCH(N)は等しく

なります．

# STCH(N) = dR1⨁ dR2⨁ ⋯ ⨁ dRN

自分自身との XOR をとると 0 となるので

# SRCH(N + 1) = STCH(N) ⨁ STCH(N)

= 0x00
となり， 0x00以外の値が得られた場合はエラーと判定できます．

Note1 : Check Sum はデータの完全性を保証するものではありません．

p. 31

ファームウェア書き込みとシリアルデバッグ
・DAP または Writer を使用する場合
ARM 用の多くの DAP (Debug Adapter) が使用可能です. (j-Link, CMSIS-DAP, ST-Link な
ど) ，ボード上のデバッグポートと DAP を次のように接続してください．

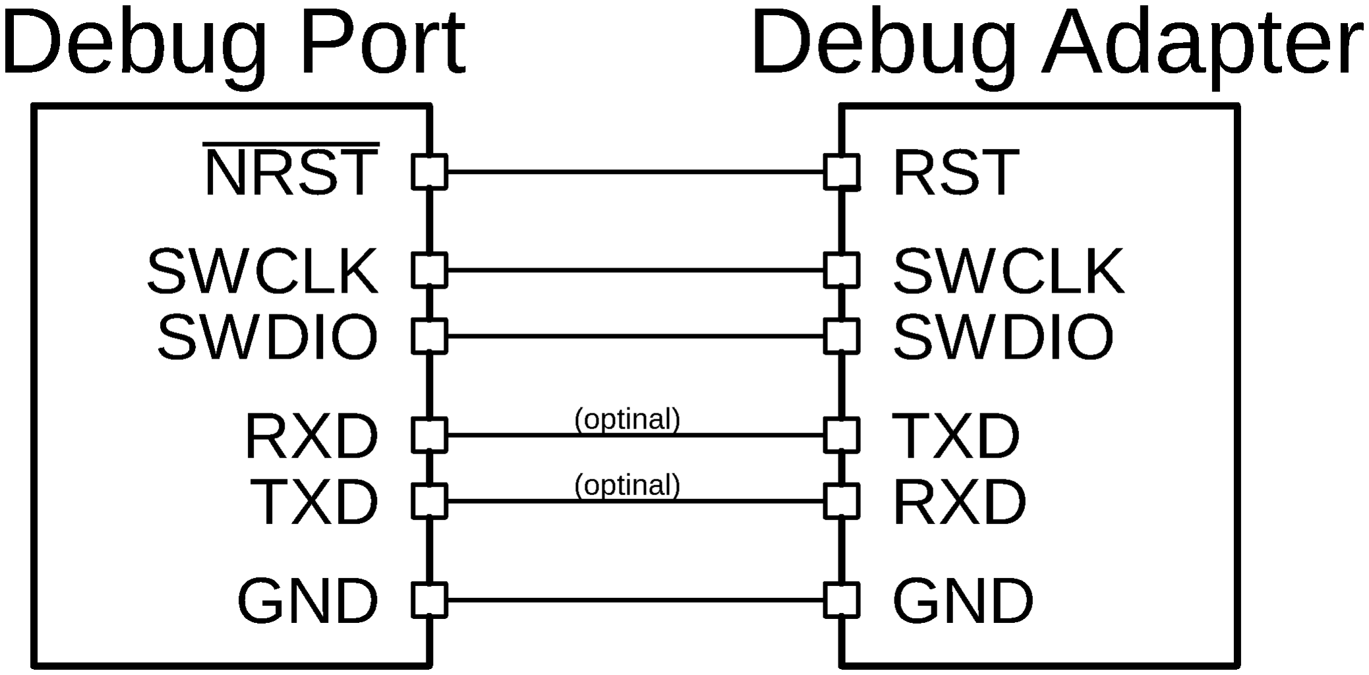
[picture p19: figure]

Fig. 9.7 DAP and Debug Port’s Connection Diagram

ファームウェア書き込み時には必要ありませんが，シリアルポートが用意されているため 簡易なデバッグ作業が行えます．本格的なデバッグの際には JTAG/SWD (SWCLK SWDIO)

を使用してデバッグを行ってください．

・DFU Bootloader を使用する場合
MPU に使用している STM32F446RE には，DFU Bootloader がシステムメモリ領域に組み込
まれています．そのため，専用の DAP や Writer を使用せずにファームウェアの書き込みが 可能です．書き込み用のアプリケーションとして STMicroelectronics DfuSe あるいは CubeProg 等が必要です．Bootloader に入るには，ボード上の S2 を押した状態でパワーオン あるいはリセットシグナルを送る必要があります．USB ケーブルが検出されますと DFU Mode に入りファームウェアが書き込める状態になります．詳しくは AN2606 STM32
microcontroller system memory boot mode (https://www.stmcu.jp/design/document/application_note/51328/) を参照してください．

p. 32
10. ソフトウェアの機能説明

■ システムクロックの設定
Mbed OS を使用する場合，STM32F446RE ではシステムクロック周波数は 180MHz で動作し ます．しかし，ハードウェア的制限を受けるため，初期状態では HSI (内部高速オシレー タ)を用いてシステムクロックが作成されます．この時，システムクロック周波数は 160MHz に設定されるため．時間指定系の API では動作が 0.1％ほど遅れます．また，PLL の設定に よっては誤差が大きくなります．これを防ぐために，ボード上の HSE XTAL (外部オシレー タ) をクロックソースとして用いる必要があります．STM32L432KC の場合は初期では MSI (内部中速オシレータ)に設定されており HSE EXTC に設定します．

・JSON を変更し HSE XTAL の使用を有効にする
Mbed OS ではクロック周辺の設定を system_clock.c 上に記述しており，設定の指示は
targets.json で行っています．以下は targets.json に記述されている，STM32F446RE の設定箇

所です．
"NUCLEO_F446RE": {
"inherits": ["FAMILY_STM32"],
"supported_form_factors": ["ARDUINO", "MORPHO"],
"core": "Cortex-M4F",
"extra_labels_add": ["STM32F4", "STM32F446xE", "STM32F446RE"],
"config": {
"clock_source": {
"help": "Mask value : USE_PLL_HSE_EXTC | USE_PLL_HSE_XTAL (need HW patch) |
USE_PLL_HSI",
"value": "USE_PLL_HSE_EXTC|USE_PLL_HSI",
"macro_name": "CLOCK_SOURCE"
}
},
"detect_code": ["0777"],
"macros_add": ["USB_STM_HAL", "USBHOST_OTHER"], "device_has_add": [
"ANALOGOUT",
"CAN",
"SERIAL_ASYNCH",
"FLASH",
"MPU"
],
"release_versions": ["2", "5"], "device_name": "STM32F446RE", "bootloader_supported": true
},

赤字表記箇所
value": "USE_PLL_HSE_EXTC|USE_PLL_HSI"
でクロックソースを指定しており，元の設定では ST-Link による MCO 入力(HSE)，あるい は HSI での動作になります．そのため当該箇所を
"value": "USE_PLL_HSE_XTAL"
に変更してください． STM32L432KC の場合は該当箇所を
value": "USE_PLL_HSE_EXTC"

に変更します．

p. 33

・クロック周辺の設定を自身で行い HSE XTAL の使用を有効にする
HAL を用いることで任意のシステムクロック周波数に変更することができますが．場合に よっては Mbed OS との相互干渉により，システムが破城する可能性があるため，非推奨と
なります．PLL 係数等の設定は STMicroelectronics STM32CubeMX を用いることを推奨しま
す，以下にシステムクロック周波数を 180MHz としたときの一例を示します．

int main (void) {

/* Put user startup code here */

RCC_OscInitTypeDef RCC_OscInitStruct = {0}; RCC_ClkInitTypeDef RCC_ClkInitStruct = {0};

/* Configure the main internal regulator output voltage */ __HAL_RCC_PWR_CLK_ENABLE(); __HAL_PWR_VOLTAGESCALING_CONFIG(PWR_REGULATOR_VOLTAGE_SCALE1);

/* Initializes the CPU, AHB and APB busses clocks */ RCC_OscInitStruct.OscillatorType = RCC_OSCILLATORTYPE_HSE; RCC_OscInitStruct.HSEState = RCC_HSE_ON; RCC_OscInitStruct.PLL.PLLState = RCC_PLL_ON; RCC_OscInitStruct.PLL.PLLSource = RCC_PLLSOURCE_HSE; RCC_OscInitStruct.PLL.PLLM = 4; RCC_OscInitStruct.PLL.PLLN = 180; RCC_OscInitStruct.PLL.PLLP = RCC_PLLP_DIV2; RCC_OscInitStruct.PLL.PLLQ = 2; RCC_OscInitStruct.PLL.PLLR = 2;
if (HAL_RCC_OscConfig(&RCC_OscInitStruct) != HAL_OK) { Error_Handler();
}

/* Activate the Over-Drive mode */
if (HAL_PWREx_EnableOverDrive() != HAL_OK) { Error_Handler();
}

/* Initializes the CPU, AHB and APB busses clocks */ RCC_ClkInitStruct.ClockType = RCC_CLOCKTYPE_HCLK|RCC_CLOCKTYPE_SYSCLK |RCC_CLOCKTYPE_PCLK1|RCC_CLOCKTYPE_PCLK2; RCC_ClkInitStruct.SYSCLKSource = RCC_SYSCLKSOURCE_PLLCLK; RCC_ClkInitStruct.AHBCLKDivider = RCC_SYSCLK_DIV1; RCC_ClkInitStruct.APB1CLKDivider = RCC_HCLK_DIV4; RCC_ClkInitStruct.APB2CLKDivider = RCC_HCLK_DIV2;

if (HAL_RCC_ClockConfig(&RCC_ClkInitStruct, FLASH_LATENCY_5) != HAL_OK) { Error_Handler();
}

/* GPIO Ports Clock Enable */
__HAL_RCC_GPIOH_CLK_ENABLE();

/* Put user startup code here */

While(1) {

/*Put user main code here */

}
}

p. 34

■ MCO の設定
FEU (STM32L432KC) は外部からの入力クロックを基に，システムクロックを作成します．
そのため MPU (STM32F446RE) 側からのクロック出力機能 MCO (Microcontroller Clock
Output) を有効にする必要があります．
出力は FEU_MCLK バスであり，MPU の PA8 から出力されます．詳しくは Fig. 8.3 と Table
8.1 を参照してください．
MCO の有効化は Mbed OS からは不可能であり，HAL を用いて行います．MPU が HSE 動

作時は次の関数を追加してください．

void MCO_Config(void)
{
GPIO_InitTypeDef GPIO_InitStruct = {0};

/* Configure the MCO1 */
HAL_RCC_MCOConfig(RCC_MCO1, RCC_MCO1SOURCE_HSE, RCC_MCODIV_1);

/* GPIO Ports Clock Enable */
__HAL_RCC_GPIOA_CLK_ENABLE();

/*Configure GPIO pin : PA8 */
GPIO_InitStruct.Pin = GPIO_PIN_8; GPIO_InitStruct.Mode = GPIO_MODE_AF_PP; GPIO_InitStruct.Pull = GPIO_NOPULL; GPIO_InitStruct.Speed = GPIO_SPEED_FREQ_LOW; GPIO_InitStruct.Alternate = GPIO_AF0_MCO; HAL_GPIO_Init(GPIOA, &GPIO_InitStruct);
}

HSI 動作時は
HAL_RCC_MCOConfig(RCC_MCO1, RCC_MCO1SOURCE_HSE, RCC_MCODIV_1)

と赤字表記された行を
HAL_RCC_MCOConfig(RCC_MCO1, RCC_MCO1SOURCE_HSI, RCC_MCODIV_2)
と変更してください．(内部オシレータが 16MHz の為) どちらの場合でも 8MHz のクロッ クパルスが PA8 から出力されます．HSI 動作時は，HSI の発振誤差と PLL の影響で
8±0.1MHz 程度になります．

p. 35

Mbed プラットフォームの変更箇所
・C++11 でプログラミングを行う
Mbed では様々なコンパイラで動作させるために C++のバージョンが C++98 になっていま す．その為，ラムダ式等の機能を使用することができません．ここでは C++11 でコンパイ ルする方法について解説します．C++のバージョンを変更するには，{project_name}¥mbed-
os¥tools¥profiles¥{profile_name}.jsom を書き換える必要があります．
例えば Build profile の一つ Relese では release.json を書き換えます．例えば ARMC6 コンパ

イラでは
"ARMC6": {
"common": ["-c", "--target=arm-arm-none-eabi", "-mthumb", "-Oz",
"-Wno-armcc-pragma-push-pop", "-Wno-armcc-pragma-anon-unions", "-DMULADDC_CANNOT_USE_R7", "-fdata-sections", "-fno-exceptions", "-MMD", "-D_LIBCPP_EXTERN_TEMPLATE(...)=", "-fshort-enums", "-fshort-wchar", "-DNDEBUG"],
"asm": [],
"c": ["-D__ASSERT_MSG", "-std=gnu99"],
"cxx": ["-fno-rtti", "-std=gnu++98"],
"ld": ["--show_full_path", "--legacyalign", "--keep=os_cb_sections"] },
の赤字部
"cxx": ["-fno-rtti", "-std=gnu++98"]

から
"cxx": ["-fno-rtti", "-std=gnu++11"]

に書き換えます．

・SPI 関係の API の改良
SPI 関係の API はバグにより，異なるチャネルであってもマイコン内で複数使用することが できません（例えば SPI1 は Master で SPI2 では Slave の様な設定）．そのため次のようなメ

ンバ関数を各クラスに追加してください．
-SPI Class
class SPI : private NonCopyable<SPI> {
public:
/* 省略 */
void free(void) {
lock();
spi_free(&_peripheral->spi); unlock();
}
/* 省略 */
};

-SPISlave Class
class SPISlave : private NonCopyable<SPISlave> { public:
/* 省略 */
void free() {
spi_free(&_spi);
}
/* 省略 */
};

p. 36

追加した free()関数はオブジェクトで行った設定を全て開放する関数です．ピン設定や割り

込みハンドラ等も開放されます．ただし，動的確保したメモリは開放されない為，メモリリ ークの危険性があることに注意してください．下に示すのは，修正した API を使ったサン

プルプログラムです．
#include “mbed.h”

SPI *spi_master;
SPISlave *spi_slvae;

enum SPIMux { SPI_MASTER, SPI_SLAVE }; void spi_switch(SPIMux mux) { spi_master->free();
spi_slave->free();

switch (mux) {
case SPI_MASTER:
delete spi_master;
spi_master = new SPISlave(SPI1_MOSI, SPI1_MISO, SPI1_SCLK, SPI1_CS); break;

case SPI_SLAVE:
delete spi_slave;
spi_slave = new SPI(SPI2_MOSI, SPI2_MISO, SPI2_SCLK, SPI2_CS); break;

default:
break;
}
}

Int main() {
While(1) {
spi_switch(SPI_MASTER);
/* SPI Master の送受信処理 */

spi_switch(SPI_SLAVE);
/* SPI Slave の送受信処理 */
}
}

p. 37

■ 専用 API (schloa-api) の概要
より開発を容易にするため，Mbed 用 API パッケージ schloa-api を用意しました．使用する 際はヘッダファイル schloa.h をインクルードし schloa_init をコールしてください

■ ADC API
ADC である ADS88xx ファミリを容易に動作される API です．
・ADC Class
Constructor & Destructor Documentation
ADC ( SPI *_spi, PinName _conv )

指定された SPI マスターとコンバート出力ピンの設定を行います．

Parameters:

_spi | SPI オブジェクトのポインタ
_cs | CS 出力ピン

~ADC ()

コンバート出力ピンを開放します．

Member Function Documentation
void setReference ( float ref )

ADC に接続されているリファレンス電圧を指定します．

Parameters:

ref リファレンス電圧 [V]

uint16_t read ()

ワンショットトリガで A/D 変換を開始し，変換結果をバイナリデータで返します．

Returns:
Raw ADC Code (0x0000 ~ 0xFFFF)

p. 38

uint16_t readVoltage ()

ワンショットトリガで A/D 変換を開始し，変換結果を電圧値で返します．

Returns:
Voltage [V]

operator uint16_t ()
ADC::read()の省略形

p. 39

■ Backup API
バックアップ API は RTC のバックアップ EPPROM 領域を利用して，データのバックアッ プを行う API です
・Backup Class
Constructor & Destructor Documentation
Backup()

RTC の初期化を行い，バックアップ機能を有効にします．

Member Function Documentation
uint32_t read (uint32_t bkp_num)

バックアップメモリからデータを取得します．

Note:
選択できる番地は RTC_BKP_DR0 が基準になります．

Parameters:

bkp_num バックアップメモリの相対番地

Returns:

読み込んだ番地のデータ

void write(uint32_t bkp_num, uint32_t data)

バックアップメモリにデータを書き込みます

Parameters:

bkp_num | バックアップメモリの相対番地
data | 書き込むデータ

p. 40

■ Communication API
Communication API は MPU と FEU 間のデータ転送を行う API です．通信プロトコルについ てはTable9.4 ～ Table9.6を参照してください．主に使用するのは CommunicationMaster Class と CommunicationSlave Class になるでしょう．

・CommunicationMaster Class
CommunicationMaster Class は MPU が FEU と通信するための API です．
Constructor & Destructor Documentation
CommunicationMaster ( SPI *_spi,
PinName _cs,
PinName _busy,
MPU_TransDataType_t *rx_data )

指定された SPI マスターと使用する受信データのアドレスを設定します．

Note:
このコンストラクタは CommunicationMaster オブジェクトを使用して，CS ピンと BUSY ピンの GPIO 入出力を操作します．

Parameters:

_spi | SPI オブジェクトのポインタ
_cs | CS 出力ピン
_busy | BUSY 入力ピン
rx_data | 受信データのポインタ

p. 41

CommunicationMaster ( SPI *_spi, PinName _cs,
PinName _busy,
)

指定された SPI マスターを設定します．

Note:
このコンストラクタは CommunicationMaster オブジェクトを使用して，CS ピンと BUSY ピンの GPIO 入出力を操作します．

Parameters:

_spi | SPI オブジェクトのポインタ
_cs | CS 出力ピン
_busy | BUSY 入力ピン

Member Function Documentation
bool transfer( MPU_TransDataType_t *rx_data )

データを転送し，受信が成功した場合は解析して書き出します．

Note:
転送が終了するまで wait 処理が入ります．

Parameters:

rx_data 受信データの構造体ポインタ

Returns:
転送の成功の有無 true：成功, false：失敗

bool transfer()

データを転送し，受信が成功した場合は解析し，受信データをコンストラクタで設定し た受信データのアドレスに代入します．

Returns:
転送の成功の有無 true：成功, false：失敗

p. 42

bool available ()

受信データが更新されたか確認します．

returns
更新の有無 true：更新, false：未更新

void attachTransferHandler ( Callback<void()> handle )

転送完了の際に呼び出されるハンドラをアタッチします．

Parameters:

handle コールされる関数のポインタ

p. 43

void attachTransferHandler ( T *obj, M method )

転送完了の際に呼び出されるハンドラをアタッチします．

Parameters:

obj | メンバ関数がコールされるオブジェクトのポインタ
method | コールされるメンバ関数のポインタ

void attachTransferErrorHandler ( Callback<void()> handle )

転送失敗の際に呼び出されるハンドラをアタッチします．

Parameters:

handle コールされる関数のポインタ

void attachTransferErrorHandler ( T *obj, M method )

転送失敗の際に呼び出されるハンドラをアタッチします．

Parameters:

obj | メンバ関数がコールされるオブジェクトのポインタ
method | コールされるメンバ関数のポインタ

void detachTransferHandler ()

転送完了の際に呼び出されるハンドラをデタッチします．

void detachTransferErrorHandler ()

転送失敗の際に呼び出されるハンドラをデタッチします．

p. 44

・CommunicationSlave Class
CommunicationSlave Class は FEU が MPU と通信するための API です． Constructor & Destructor Documentation
CommunicationMaster ( SPISlave *_spi,
PinName _busy,
FEU_TransDataType_t *rx_data )

指定された SPI マスターと使用する受信データのアドレスを設定します．

Note:
このコンストラクタは CommunicationSlave オブジェクトを使用して，CS ピンと BUSY ピンの GPIO 入出力を操作します．

Parameters:

_spi | SPI オブジェクトのポインタ
_busy | BUSY 入力ピン
rx_data | 受信データのポインタ

CommunicationMaster ( SPISlave *_spi, PinName _busy,
)

指定された SPI マスターを設定します．

Note:
このコンストラクタは CommunicationSlave オブジェクトを使用して，CS ピンと BUSY ピンの GPIO 入出力を操作します．

Parameters:

_spi | SPI オブジェクトのポインタ
_busy | BUSY 入力ピン

p. 45

Member Function Documentation
bool transfer ( FEU_TransDataType_t *rx_data )

データを転送し，受信が成功した場合は解析して書き出します．

Note:
転送が終了するまで wait 処理が入ります．

Parameters:

rx_data 受信データの構造体ポインタ

Returns:
転送の成功の有無 true：成功, false：失敗

bool transfer ()

データを転送し，受信が成功した場合は，解析し，受信データをコンストラクタで設定 した受信データのアドレスに代入します．

Note:
転送が終了するまで wait 処理が入ります．

Returns:
転送の成功の有無 true：成功, false：失敗

bool available ()

受信データが更新されたか確認します．

returns
更新の有無 true：更新, false：未更新

void attachTransferHandler ( Callback<void()> handle )

転送完了の際に呼び出されるハンドラをアタッチします．

Parameters:

handle コールされる関数のポインタ

p. 46

void attachTransferHandler ( T *obj, M method )

転送完了の際に呼び出されるハンドラをアタッチします．

Parameters:

obj | メンバ関数がコールされるオブジェクトのポインタ
method | コールされるメンバ関数のポインタ

void attachTransferErrorHandler ( Callback<void()> handle )

転送失敗の際に呼び出されるハンドラをアタッチします．

Parameters:

handle コールされる関数のポインタ

void attachTransferErrorHandler ( T *obj, M method )

転送失敗の際に呼び出されるハンドラをアタッチします．

Parameters:

obj | メンバ関数がコールされるオブジェクトのポインタ
method | コールされるメンバ関数のポインタ

void detachTransferHandler ()

転送完了の際に呼び出されるハンドラをデタッチします．

void detachTransferErrorHandler ()

転送失敗の際に呼び出されるハンドラをデタッチします．

p. 47

・MPUToFEUFitting Class
MPUToFEUFitting Class は FEU 用のデータフォーマットを基に，送信データの作成，そし て，受信データの解析を行う API です．
Constructor & Destructor Documentation
MPUToFEUFitting ( FEU_TransDataType_t *data )

データ解析結果を代入する構造体ポインタを指定します．

Parameters:

data 解析結果を代入する構造体ポインタ

MPUToFEUFitting ()

データフィッティングの際に使用するバッファを初期化します．

Member Function Documentation
void fitting ( uint8_t *msg )

設定値をメッセージとしてフィッティングし書き出します．
Parameters:

msg 書き出されるメッセージの配列ポインタ

void fitting ()

設定値をメッセージとしてフィッティングします．

void setAccumulationBit ( bool en )
Config Byte の AccumulationBit の設定を行います．

Parameters:
en true:有効, false:無効

void accumulationEnable ()
Config Byte の AccumulationBit を有効に設定します．

void accumulationDisable ()
Config Byte の AccumulationBit を無効に設定します．

p. 48

bool isAccumulationEnable ( FEU_TransDataType_t *data )

受信データの構造体から AccumulationBit のみを取り出します．

Parameters:

data 受信データの構造体ポインタ

bool isAccumulationEnable ()

コンストラクタで設定した受信データから AccumulationBit のみを取り出します．

Returns::
AccumulationBit true:有効 false:無効

void setDrakCorrectionBit ( bool en )
Config Byte の DrakCorrectionBit の設定を行います．

Parameters:
en true:有効, false:無効

void drakCorrectionEnable ()
Config Byte の DrakCorrectionBit を有効に設定します．

void drakCorrectionDisable ()
Config Byte の DrakCorrectionBit を無効に設定します．

bool isDrakCorrectionEnable ( FEU_TransDataType_t *data )

受信データの構造体から DrakCorrectionBit のみを取り出します．

Parameters:

data 受信データの構造体ポインタ

bool isDrakCorrectionEnable ()

コンストラクタで設定した受信データから DrakCorrectionBit のみを取り出します．

Returns::
DrakCorrectionBit true:有効 false:無効

p. 49

void setAccumulationModeBit ( AccumulationMode mode ) Config Byte の AccumulationModeBit の設定を行います．

Parameters:

mode 蓄積モード

void oneshotMode ()
Config Byte の AccumulationModeBit を Oneshot に設定します．

void continuousMode ()
Config Byte の AccumulationModeBit を Continuous に設定します．

AccumulationMode getAccumulationMode ( FEU_TransDataType_t *data )

受信データの構造体から AccumulationModeBit のみを取り出します．

Parameters:

data 受信データの構造体ポインタ

Returns::
AccumulationModeBit

AccumulationMode getAccumulationMode ()

コンストラクタで設定した受信データから AccumulationModeBit のみを取り出します

Returns:
AccumulationModeBit

void setResetBit ( OperationMode mode ) Config Byte の ResetBitt の設定を行います．

Parameters:

mode 動作モード

p. 50

void resetOperationMode ()
Config Byte の ResetBitt を ResetOperation に設定します．

void normalOperationMode ()
Config Byte の ResetBit を NormalOperation に設定します．

OperationMode getOperationMode ( FEU_TransDataType_t *data )

受信データの構造体から ResetBit のみを取り出します．

Parameters:

data 受信データの構造体ポインタ

Returns::
ResetBit

OperationMode getOperationMode ()

コンストラクタで設定した受信データから ResetBit のみを取り出します

Returns:
ResetBit

void setAverageNumber ( uint8_t num )

算術平均処理する回数を設定します．

Note:
0 を指定すると算術平均処理を行いません．

Parameters:

num 平均回数

p. 51

uint8_t getAverageNumber(FEU_TransDataType_t *data)

受信データの構造体から平均回数のみを取り出します．

Parameters:

data 受信データの構造体ポインタ

Returns::

平均回数

uint8_t getAverageNumber()

コンストラクタで設定した受信データから平均回数のみを取り出します．

Returns:

平均回数

void setConfigByte ( FEU_ConfigDataType_t conf ) Config Byte を書き込みます．

Parameters:
conf ConfigByte の構造体

void setConfigByte();
Config Byte を書き込みます．

Note:
ConfigByte の各 bit の設定後にコールしてください．コールしない場合，設定が反映さ

れずにメッセージが書き出されます

p. 52

FEU_ConfigDataType_t getConfigByte ( FEU_TransDataType_t *data )

受信データの構造体から ConfigByte のみを取り出します．

Parameters:

data 受信データの構造体ポインタ

Returns::
ConfigByte

FEU_ConfigDataType_t getConfigByte()

コンストラクタで設定した受信データから ConfigByte のみを取り出します

Returns:
ConfigByte

void setAccumulationTime ( uint32_t us )

蓄積時間を設定します．

Parameters:
us 蓄積時間[us]

uint32_t getAccumulationTime(FEU_TransDataType_t *data)

受信データの構造体から蓄積時間のみを取り出します．

Parameters:

data 受信データの構造体ポインタ

Returns::
蓄積時間[us]

uint32_t getAccumulationTime ()

コンストラクタで設定した受信データから蓄積時間のみを取り出します．

Returns:
蓄積時間[us]

p. 53

void setTransData(FEU_TransDataType_t *data)

構造体を代入し全ての設定を行います．

Parameters:

data 送信データの構造体ポインタ

bool messageAnalyze ( uint8_t *msg, FEU_TransDataType_t *data )

チェックサムを調べ，メッセージが有効であれば，メッセージを解析し，解析したデー タを書き出します．

Parameters:

msg | 受信したメッセージの配列ポインタ
data | 書き出される解析結果の構造体ポインタ

Successful reception (true : success , false : failure)

p. 54

・FEUToMPUFitting Class
FEUToMPUFitting Class は MPU 用のデータフォーマットを基に，送信データの作成，そし て，受信データの解析を行う API です．
Constructor & Destructor Documentation
FEUToMPUFitting ( MPU_TransDataType_t *data )

データ解析結果を代入する構造体ポインタを指定します．

Parameters:

data 解析結果を代入する構造体ポインタ

FEUToMPUFitting ()

データフィッティングの際に使用するバッファを初期化します．

Member Function Documentation
void fitting ( uint8_t *msg )

設定値をメッセージとしてフィッティングし書き出します．
Parameters:

msg 書き出されるメッセージの配列ポインタ

void fitting ()

設定値をメッセージとしてフィッティングします．

void setPixData ( uint16_t *data )

送信するピクセルデータを設定します．

Note：
値の代入は行わず，先頭アドレスのみを登録します．そのため fitting をコールするまで

ピクセルデータの変更は行わないでください．

Parameters:

data ピクセルデータの配列ポインタ

p. 55

void getPixData ( MPU_TransDataType_t *data, uint16_t *pix_buf )

受信データの構造体からピクセルデータのみを取り出します．

Parameters:

data | 受信データの構造体ポインタ
pix_buf | ピクセルデータの配列ポインタ

void getPixData ( uint16_t *pix_buf )

コンストラクタで設定した受信データからピクセルデータのみを取り出します．

Parameters:

pix_buf ピクセルデータの配列ポインタ

void setTransData(MPU_TransDataType_t *data)

構造体を代入し全ての設定を行います．

Parameters:

data 送信データの構造体ポインタ

bool messageAnalyze(uint8_t *msg, MPU_TransDataType_t *data)

チェックサムを調べ，メッセージが有効であれば，メッセージを解析し，解析したデー タを書き出します．

Parameters:

msg | 受信したメッセージの配列ポインタ
data | 書き出される解析結果の構造体ポインタ

Returns:
Successful reception (true : success , false : failure)

p. 56

・Fitting Class
Fitting Class はデータフィッティングの際に使用するバッファの管理を容易にする API です．
Template Class の為，型指定が必要です．

Constructor & Destructor Documentation
template<class T> Fitting(uint32_t msg_size)

指定したデータ長 (型依存) の T 型の動的配列を作成します．

Parameters:
msg_size 配列の要素数

template<class T> ~Fitting()

確保したメモリを開放します．

Parameters:
msg_size 配列の要素数

Member Function Documentation
template<class T> T checkSum(T *msg, uint32_t length)

指定した要素までの Check Sum を計算します

Parameters:

msg | チェックする配列ポインタ
length | チェックする要素数

Returns
Check Sum ( 0:Non Error, other:Error )

template<class T> T checkSum()

作成した動的配列の最後の要素を抜いた Check Sum を計算します．

Returns
Check Sum ( 0:Non Error, Other:Error )

p. 57

template<class T> uint32_t size()

作成した動的配列の要素数を返します．

Note:
確保されるバイト長は T 型のバイト長を乗算する必要があります．

Returns
Byte Length

template<class T> T front()

作成した動的配列の先頭要素を参照します．

Returns

先頭要素

template<class T> T back()

作成した動的配列の最後尾要素を参照します．

Returns

最後尾要素

template<class T> T *data()

作成した動的配列の先頭要素のポインタを参照します．

Returns

先頭要素のポインタ

template<class T> T & operator [](uint32_t n)

作成した動的配列の指定した要素を参照します．(オペレータのオーバーロード)

Exsample Code:
int main() {
Fitting<int> obj(3);
obj[2] = 114514;
printf(“obj[2] = %d¥n¥r” obj[2]); //Result : obj[3] = 114514 }

p. 58

■ DebugPort API
Cortex コアが持つ ITM 機能によって printf 形式のデバッグを提供する API です．USART を

用いたデバッグより高速に行えます．
・DebugPort Class
Constructor & Destructor Documentation
DebugPort(const char *name)

ITM デバッグを有効にします．

Note:
JTAG デバッガとマイコンの SWCLK SWDIO SWO を接続する必要があります．

Parameters:
name ポート名

Member Function Documentation int putc(int c)

文字出力を行います．

Parameters:

c | 文字

Returns:

エラー

int printf(const char* format, ...)

フォーマットに従い，文字列を出力します．
Note:
JTAG デバッガとマイコンの SWCLK SWDIO SWO を接続する必要があります．

Parameters:
printf 準拠

Returns:

出力した文字数

p. 59

■ DrawSpectrum API
専用 GUI DrawSpectrum との相互通信機能を提供する API です．

・DrawSpectrum Class
Constructor & Destructor Documentation
DrawSpectrum(USBSerial *obj, DrawSpectrum_TransDataType_t *rx_data)

初期設定を行います．

Note:
Mbed OS2 版の USBSerial API が必要になります．

Parameters:
obj | USBSerial のオブジェクトポインタ
rx_data | 受信データの構造体ポインタ

DrawSpectrum(USBSerial *obj)

初期設定を行います．受信バッファは動的確保されます．

Note:
Mbed OS2 版の USBSerial API が必要になります．

Parameters:
obj USBSerial のオブジェクトポインタ

Member Function Documentation
void send(DrawSpectrum_TransDataType_t *tx_data)

再設定しデータをパケット転送します．

Parameters:

tx_data 出力データの構造体ポインタ

void send()

設定済みのデータをパケット転送します

p. 60

DrawSpectrum_DataStatusType read(DrawSpectrum_TransDataType_t *rx_data)

受信したパケットデータを解析し，各データに分別します．

Parameters:

rx_data 受信データの構造体ポインタ

Returns:

データステータス

DrawSpectrum_DataStatusType read(DrawSpectrum_TransDataType_t *rx_data)

受信したパケットデータを解析し，各データに分別します． 受信データはコンストラクタで指定したアドレスへコピーされます．

Returns:

データステータス

void attachPacketReceiveHandler(Callback<void()> handle)

データパケット受信時にコールされるハンドラを指定します．

Parameters:

handle コールされる関数のポインタ

template<typename T, typename M> void attachPacketReceiveHandler(T *obj, M method)

データパケット受信時にコールされるハンドラを指定します．

Parameters:

obj | メンバ関数がコールされるオブジェクトのポインタ
method | コールされるメンバ関数のポインタ

p. 61

・DrawSpectrumAnalyze Class
Constructor & Destructor Documentation DrawSpectrumAnalyze(DrawSpectrum_TransDataType_t *rx_data)

初期設定を行い，バッファを初期化します．

Parameters:

rx_data 受信データの構造体ポインタ

DrawSpectrumAnalyze()

初期設定を行い，バッファを初期化します．

Member Function Documentation
殆どが Communication API と同じ形をとっています．以下は追加されたメンバです．
void setPixDataOffset(uint16_t *data);

ピクセルデータのオフセット値を設定します．

Parameters:

data オフセットデータ配列のポインタ

virtual uint32_t pixDataNormalizeation(uint32_t ch);

ピクセルデータを正規化後，転送データに変換します．

Note:

正規化処理はダーク減算後，指定ピクセルでの理論上の最大感度に対する相対値の百 分率に変換します．一般的な相対感度とは異なることに注意してください． 転送データは正規化値の 100 倍の値になります．

# DD = DD × 10000 AA _MM MM_CCCC CC − OOOOOO

Parameters:

data オフセットデータ配列のポインタ

void getLEDBrightness(DrawSpectrum_TransDataType_t *data, float *brightness)

受信データから各 LED の明度情報を取得します．

p. 62

Parameters:

data | 受信データの構造体ポインタ
brightness | LED のチャネル分の明度データのポインタ

void getLEDBrightness(float *brightness)

受信データから各 LED の明度情報を取得します．

Parameters:

brightness LED のチャネル分の明度データのポインタ

std::time_t getTime(DrawSpectrum_TransDataType_t *data)

受信データから時刻情報を取得します．

Parameters:

data 受信データの構造体ポインタ

Returns:
UNIX 時間

std::time_t getTime()

受信データから時刻情報を取得します．

Returns:
UNIX 時間

p. 63

■ FastOut API
FastOut Class は直接的にレジスタを操作することで GPIO の出力の高速化を図った API で

す．ハードウェアの依存性が高いため汎用的な使用ができません．

・FastOut Class
Constructor & Destructor Documentation
FastOut ( PinName _pin )

指定した GPIO ピンの初期化を行い，出力ポートに設定します．

Parameters:
_pin 出力ピン

~FastOut()

出力に設定したピンを開放します

Member Function Documentation
void write ( uint32_t value )

GPIO ピンの出力値を設定します．

Parameters:
value 0 : Low, Other : High

void toggle ()

GPIO ピンの出力値をトグルします．

uint32_t read ()

GPIO ピンの出力状態を返します．

Returns:
Pin Status 0 : Low, Other : High

p. 64

FastOut &operator= (uint32_t value) FastOut::write()の省略形

Ex)
Int main() {
FastOut out (LED1);
out = 1; //LED1 High
}

FastOut &operator= (FastOut& rhs)

オブジェクトから出力状態をコピーし出力状態を変更する FastOut::write()の省略形

operator uint32_t()
FastOut::read ()の省略形

p. 65

■ LEDDrive API
LED 制御用の API です．PWM によって調光します．
・LEDDrive Class
Constructor & Destructor Documentation LEDDrive(uint32_t pin_num, ...)

出力ピンの設定を行います.

Parameters:
pin_num | 出力ピンの総数
… | (PinName 型)出力ピン番号(可変長)

virtual ~LEDDrive()

出力ピンを開放します．

Member Function Documentation
uint32_t size()

指定した出力ピンの総数を取得します．

Returns:

ピンの総数

void write(uint32_t pin_num, float val)

指定したピンの Duty 比を設定します

Parameters:
pin_num | ピン番号
val | Duty 比
void write(float *val)

全てのピンの Duty 比を設定します

Parameters:

val | Duty 比配列のポインタ

void setFrequency(uint32_t pin_num, float frequency)

p. 66

指定したピンの周波数を変更します．

Parameters:
pin_num | ピン番号
frequency | 周波数

void setFrequency(float *frequency)

全てのピンの周波数を変更します．

Parameters:

frequency 周波数配列のポインタ

float read(uint32_t pin_num)

指定したピンの Duty 比を取得します．

Parameters:
pin_num ピン番号

float & operator [](int n)
LEDDrive::write と LEDDrive::read の省略形 Parameters:
n | ピン番号

Ex)
Int main() {
LEDDrive out (2, PB_0, PB 1);
Out[1] = Out[0]; //out.write(1, out.read(0)); }

p. 67

■ LiquidCrystal API
printf 形式で LCD に文字列表示機能を提供する API です．ST7032 互換のドライバ IC にの

み対応します．

・LiquidCrystal Class
Constructor & Destructor Documentation
LiquidCrystal(I2C *i2c, uint8_t addr)

指定された I2C マスターと使用するスレーブアドレスを設定します．

Parameters:

i2c | I2C のオブジェクトポインタ
addr | スレーブアドレス

Member Function Documentation
void init()

LCD の初期化を行います．

void clear()

文字の消去を行います．

void home()

カーソルをホーム地点に移動させます．

void setCursor(uint32_t col, uint32_t line)

カーソルを指定の位置に移動させます．

Parameters:

col | 移動する列
line | 移動する行

void shift(int32_t shift)

指定した文字分表示を左右にシフトさせます．

Parameters:
shift シフトさせる列数 (+ : 右 - : 左)

p. 68

void setContrast(uint8_t val)

コントラストを設定します

Parameters:
val コントラスト(7bit)

int putc(int c)

カーソル地点に文字出力を行います．

Parameters:

c | 文字

Returns:

エラー

int printf(const char* format, ...)

フォーマットに従い，カーソル地点に文字列を出力します．

Parameters:
printf 準拠

Returns:

出力した文字数

p. 69

■ SoftPWMOut API
ソフトウェアによって PWM 機能を提供する API です．ハードウェアに依存せず PWM 出

力が可能です．

・SoftPWMOut Class
Constructor & Destructor Documentation
SoftPWMOut(PinName pin)

出力ピンの設定を行います．

Parameters:

pin ピン番号

Member Function Documentation
void start()

タイマ割り込みを開始し，出力を有効にします．

void free()

タイマ割り込みを無効にし，ピンを開放します．

void write(float value)

Duty 比を設定します．

Parameters:
value Duty 比

float read()

現在の Duty 比を取得します．

Returns:
Duty 比

p. 70

void period(float seconds)

パルス周期を設定します

Parameters:
seconds パルス周期[s]

void period(float ms)

パルス周期を ms 単位で設定します

Parameters:
ms パルス周期[ms]

void period(float us)

パルス周期を µs 単位で設定します

Parameters:
us パルス周期[µs]

void pulsewidth(float seconds)

パルス幅を設定します．

Parameters:
seconds パルス幅[s]

void pulsewidth(float ms)

パルス幅を ms 単位で設定します．

Parameters:
ms パルス幅[ms]

void pulsewidth(float us)

パルス幅を µs 単位で設定します．

Parameters:
us パルス幅[µs]

p. 71

SoftPWMOut &operator=(float value) SoftPWMOut::write の省略形

Parameters:
value Duty 比

Ex)
Int main() {
SoftPWMOut out (LED1);
out.start();
out = 0.5f; //out.write(0.5f);
}

SoftPWMOut &operator=(SoftPWMOut &rhs) SoftPWMOut::write の省略形

Parameters:
rhs SoftPWMOut のオブジェクトポインタ

p. 72

■ SystemTicker API
SystemTicker API は System Timer を利用してタイマ割り込みを発生される API です， System Timer を使用する都合上，時間計の API(wait, timer 等)は使用不可になります． ・System Ticker Class
Constructor & Destructor Documentation
SystemTicker()

カウンタを初期化します

~SystemTicker()

タイマを開放し，割り込みハンドラをデタッチします．

Member Function Documentation
void attach ( Callback<void()> handle, float s )

タイマ割り込みの際にコールされるハンドラをアッタッチし，インターバル時間を[s]

単位で指定します．

Parameters:

handle | コールされる関数ポインタ
s | インターバル時間[s]

void attach ( T obj, M *method, float s )

タイマ割り込みの際にコールされるハンドラをアッタッチし，インターバル時間を[s]

単位で指定します．

Parameters:

obj | メンバ関数がコールされるオブジェクトのポインタ
method | コールされるメンバ関数のポインタ
s | インターバル時間

p. 73

void attach_ms ( Callback<void()> handle, float ms )

タイマ割り込みの際にコールされるハンドラをアッタッチし，インターバル時間を[ms]

単位で指定します．

Parameters:

handle | コールされる関数ポインタ
ms | インターバル時間[s]

void attach_ms ( T obj, M *method, float ms )

タイマ割り込みの際にコールされるハンドラをアッタッチし，インターバル時間を[ms]

単位で指定します．

Parameters:

obj | メンバ関数がコールされるオブジェクトのポインタ
method | コールされるメンバ関数のポインタ
ms | インターバル時間

void attach_us ( Callback<void()> handle, float us )

タイマ割り込みの際にコールされるハンドラをアッタッチし，インターバル時間を[us]

単位で指定します．．

Parameters:

handle | コールされる関数ポインタ
ms | インターバル時間[us]

void attach_us ( T obj, M *method, float us )

タイマ割り込みの際にコールされるハンドラをアッタッチし，インターバル時間を[us]

単位で指定します．

Parameters:

obj | メンバ関数がコールされるオブジェクトのポインタ
method | コールされるメンバ関数のポインタ
ms | インターバル時間[us]

p. 74

void detach()

タイマ割り込みの割り込みハンドラをデタッチします．

static void init ( uint32_t cnt )

タイマの最大カウント数を設定し，タイマを初期化します．

Parameters:

cnt タイマカウンタの最大値

Temperature API
温度センサの制御を提供する API です．ADT7410 にのみ対応します．

p. 75

■ Sound API
音声出力機能を提供する API です．現在は矩形信号にのみ対応します．

・Sound Class
Constructor & Destructor Documentation
Sound(PinName _pin)

音声出力ピンの初期化を行います．

Note:
SoftPWMOut API により音声作成を行うため，ピンによる制限がありません．

Parameters:
_pin ピン番号

Member Function Documentation
void toneWrite(uint8_t note, uint8_t verocity)

指定したノート番号の周波数とヴェロシティの強さの矩形波を出力します．

Parameters:
note | ノート番号(7bit)
verocity | ヴェロシティ(7bit)

void set(float frq, float level)

指定した周波数と Duty 比の矩形波を出力します．

Parameters:
frq | 周波数
level | Duty 比

void free()

ピンを開放します.

p. 76

Sound &operator=(float frq) Sound::set の半省略形

Note:
Duty 比は 50%固定出力になります．

Parameters:
frq 周波数

p. 77

■ Spectoro API
Spectoro API はマイクロ分光器を容易に動作させる API です．システムタイマを使うことで 不具合が生じる場合は NOT_USING_SYSTICK を定義してください．
・Spectro Class
Constructor & Destructor Documentation
Spectro ( PinName clk_pin, PinName start_pin )

分光器に対する入出力設定と設定の初期化を行います．

Note:
DigitalOut オブジェクトあるいは FastOut オブジェクトを使用して CLK ピンと ST ピン

の入出力設定を行います．

Parameters:

clk_pin | クロックパルスピン
Start_pin | スタートパルスピン

~Spectro ()

分光器に対する入出力設定を開放します．また，読み込みハンドラをデタッチします．

Note:
DigitalOut オブジェクトあるいは FastOut オブジェクトを使用して CLK ピンと ST ピン

の入出力の開放を行います．

Member Function Documentation
void startRead ();

読み込み処理等の割り込みを許可し，蓄積を開始します．

Note:
SystemTicker オブジェクトあるいは Ticker オブジェクトでタイマ割り込みを有効にし

ます．また読み込み終了まで何度コールしても問題ありません．

bool notifyReadComplete ()

全ピクセルの読み込み完了を通知します．

Returns:
読み込みの完了 true:完了 false:未了 (読み込みを行っていない場合も有)

p. 78

bool setClockFrequency ( float clk_frq )

クロック周波数を設定します．

Note:

蓄積時間はクロック周波数に依存するため，出来るだけクロック周波数を大きくして ください．クロック周波数の最大値はハードウェア依存であり，自身で最大値を計測す る必要があります．設定の可不可はあくまでも理論値で判定しています．

Parameters:
clk_frq クロック周波数[Hz]

Returns:
設定の可不可 true:設定可能 false:設定不可能

bool setAccumuTime ( float us )

蓄積時間をマイクロ秒単位で設定します．

Note:
setFrequency でクロック周波数を設定してからコールしてください

Parameters:
us 蓄積時間[us]

Returns:
設定の可不可 true:設定可能 false:設定不可能

void setCalibCoeff ( float *coeff )

5 次近似の波長補正係数を設定します．

Note:

詳しくは分光器の補正係数リストを参照してください．

Parameters:

coeff 波長補正係数の配列ポインタ

p. 79

float waveLengthConvert ( uint32_t pix_num )

設定した波長補正係数を基に，ピクセル番号から波長を算出します.
Note:
setCalibCoeff で補正係数を設定してからコールしてください.

Parameters:
pix_num ピクセル番号 ( 0, 1, 2, … ,287 )

Returns:
設定の可不可 true:設定可能 false:設定不可能

void attachReadHandler ( Callback<void()> handle )

ピクセルデータが分光器から出力される際にコールされるハンドラをアッタッチしま す．

Note:

このハンドラ内でピクセルの読み込みを行ってください．

Parameters:

handle コールされる関数のポインタ

void attachReadHandler ( T *obj, M method )

ピクセルデータが分光器から出力される際にコールされるハンドラをアッタッチしま す．

Note:

このハンドラ内でピクセルの読み込みを行ってください．

Parameters:

obj | メンバ関数がコールされるオブジェクトのポインタ
method | コールされるメンバ関数のポインタ

p. 80

■ SwitchStatus API
スイッチ入力のチャタリング除去機能や長押し検出機能を提供する API です．

・SwitchStatus Class
Constructor & Destructor Documentation
SwitchStatus(uint32_t pin_num, ...)

スイッチ入力ピンの初期化を行います．

Parameters:

pin_num | スイッチ入力ピンの総数
... | (PinName 型)ピン番号(可変長)

virtual ~SwitchStatus()

全てのスイッチ入力ピンを開放します．

Member Function Documentation
void mode(PinMode pull_mode = PullDefault)

スイッチ入力ピンのプルモードを設定します．

Note:
プルモードは read 時の論理モードに直結します．

Parameters:
pull_mode プルモード

void startSampring(uint32_t us = 30000)

サンプリング周期を µs 単位で設定します．

Parameters:

us | サンプリング周期[µs]

p. 81

bool read(uint32_t sw_num)

スイッチの状態を取得します．

Parameters:
sw_num スイッチ番号

Returns:
スイッチの状態(押しているとき:True)

bool longPressRead(uint32_t sw_num, uint32_t th)

スイッチの長押し状態を取得します．

Parameters:
sw_num | スイッチ番号
th | 閾値時間[µs]

Returns:
スイッチの状態(長押ししている状態:True)

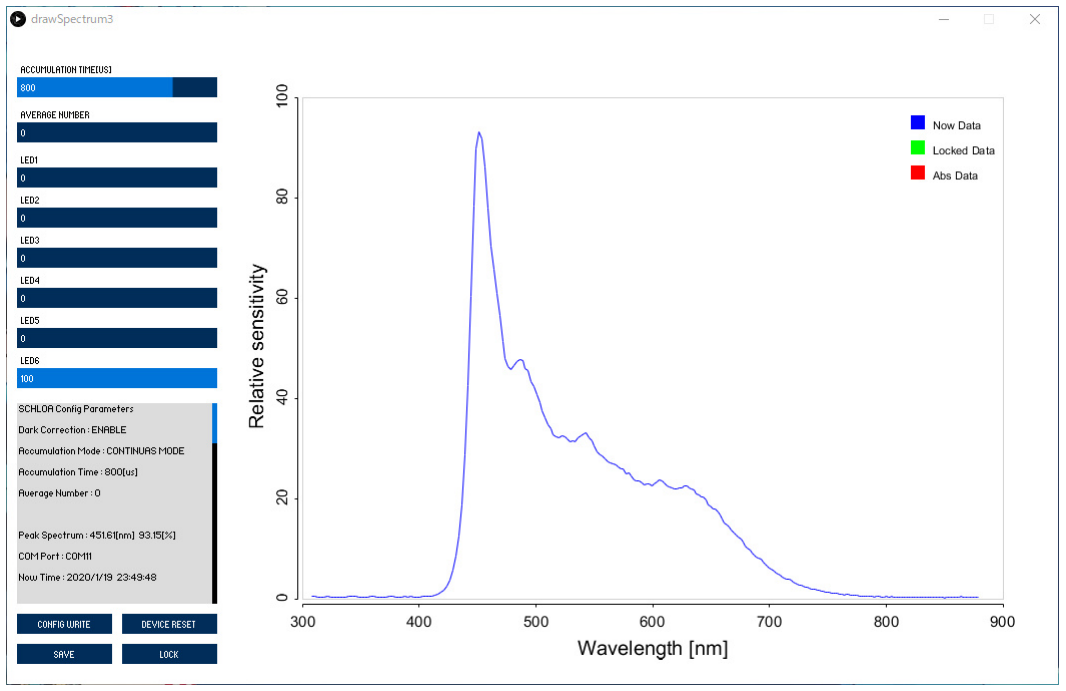
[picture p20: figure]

p. 82

■ スペクトル表示アプリケーション drawSpectrum
Windows 用にスペクトル表示アプリケーションを用意しました．GUI 操作でスペクトルの

表示やスペクトルの保存，露出設定が可能です．

Fig. 10.1 Original GUI “DrawSpectrum”

言語は Java で開発されています．仕様上，相対感度と表示されていますが，これは各ピク

セルにおける最大感度に対する相対値を取っています．修正が必要になります．

p. 83

・データフォーマット
データブロック長は可変長です．シリアル通信を使って文字列で送信してください．開始文 字は’$’(ドル記号) ，区切り文字は ‘,’(カンマ)，終了文字は’¥n’(LF 文字)です．文字形式は
ASCII です．

・送信データフォーマット

Tabel 10.1 drawSpectrum Send Data Formats
String | S0 | S1 | S3 | S4 | … | S291 | S293
Data | ‘$’ | CNF_C | ACM_T | PIX0 | … | PIX287 | “¥n”

“$” : Start Character

CNF：Config Characters
Tabel 10.2 CONF Character Data Formats
Character | C0 | C1 | C2 | C3 | C4 | C5
Data | AEN | DEN | AMOD | RSV | AVERAGEN

AEN : Accumulation Enable
‘0’ : Disable
‘1’ : Enable

DEN : Dark Correction Enable ‘0’ : Disable
‘1’ : Enable

AMOD : Accumulation Mode
‘0’ : Oneshot Mode
‘1’ : Continuous Mode

RSV：Reserved

AVERAGEN : Average Number
“01” ~ “17”

ACM_T：Accumulation Time

p. 84

PIXn : Pixel Datas (Number of n)

’¥0’：End Character

’,’： Delimiter

・受信データフォーマット

Table 10.2 drawSpectrum Receive Data Formats
String | S0 | S1 | S2 | S3 | S4 | … | S9 | S10 | 11
Data | ‘$’ | RST | AVERAGEN | ACM_T | LED0 | … | LED5 | TIME | “¥n”

“$” : Start Character

RST：Reset Flag
‘0’ : Normal Operation
‘1’ : Reset Operation

AVERAGEN : Average Number
“01” ~ “17”

ACM_T：Accumulation Times

LEDn : LED brightness(Number of n)

’¥0’：End Character

’,’： Delimiter

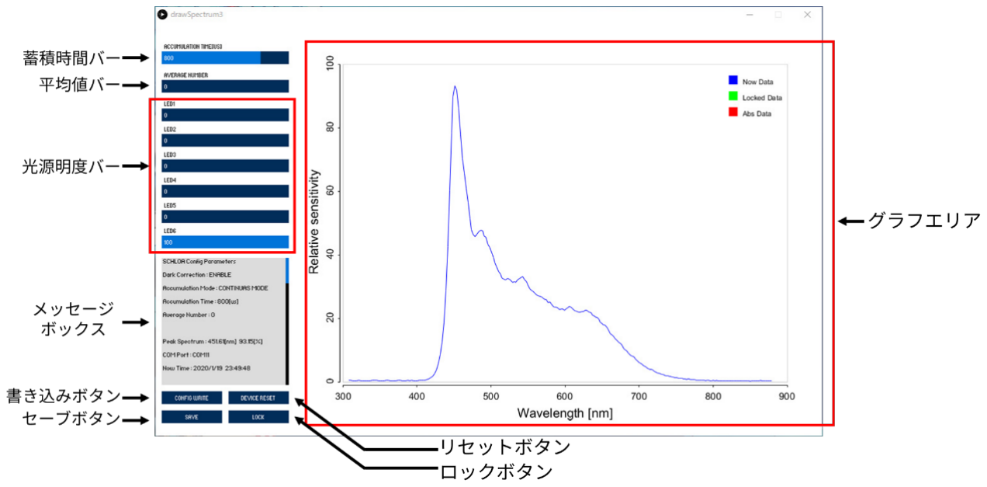
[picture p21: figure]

p. 85

・操作方法
・各部名称

Fig. 10.2 Controller Names

蓄積時間バー：蓄積時間の設定値の操作
平均値バー：平均数の設定値の操作
光源明度バー：各光源の明度の操作
メッセージボックス：測定条件の表示
書き込みボタン：設定値の送信
リセットボタン：リセット命令の送信
セーブボタン：csv データと png データの保存

ロックボタン：スペクトルを固定表示した状態で現在のスペクトルを表示

・キャリブレーション
キャリブレーションは波長にのみ対応しています．
data ファイル内の wavelength_calibration_coefficient.csv 内の 5 つの補正係数を変更すること

で波長補正が可能です．補正係数はマイクロ分光器購入時の付属資料に記載されています．

・吸収スペクトル測定
ロックボタンを押すと押す前のスペクトルを入射スペクトル，押した後のスペクトルを透 過(反射)スペクトルとして自動的に吸収スペクトルを算出します．また，蓄積時間の差異も

自動的に補正されます．

p. 86

・測定データの保存
セーブボタンを押すと測定値を CSV 形式でグラフエリアを PNG 形式で保存することが可 能です．ファイル名は SPC 年月日時分秒.拡張子でドキュメント内の DrawSpectrum に保存

されます．

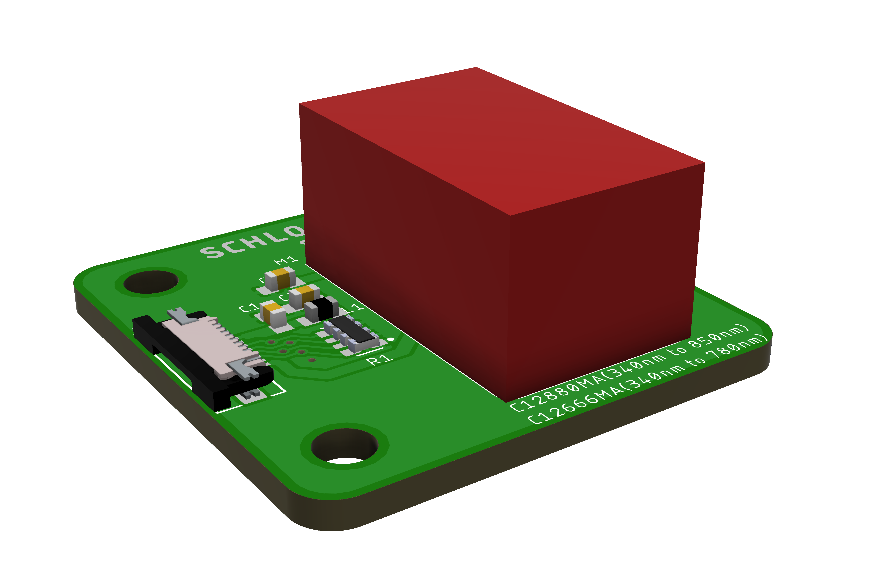
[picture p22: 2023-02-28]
Eagle/chlorophyll_analyzer_spectorometer/chlorophyll_analyzer_spectorometer_rendering.png

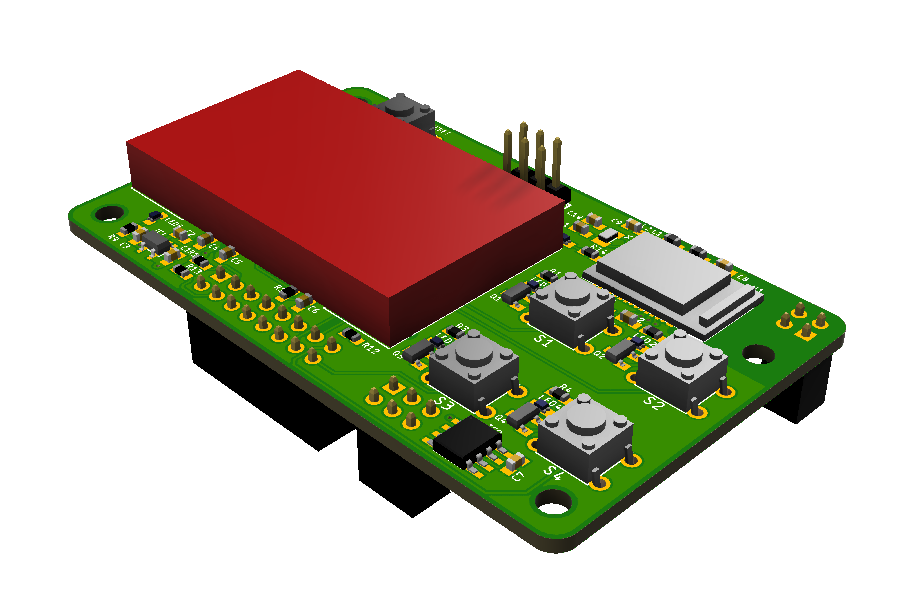
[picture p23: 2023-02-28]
Eagle/chlorophyll_analyzer_attachment/chlorophyll_analyzer_attachment_rendering.png

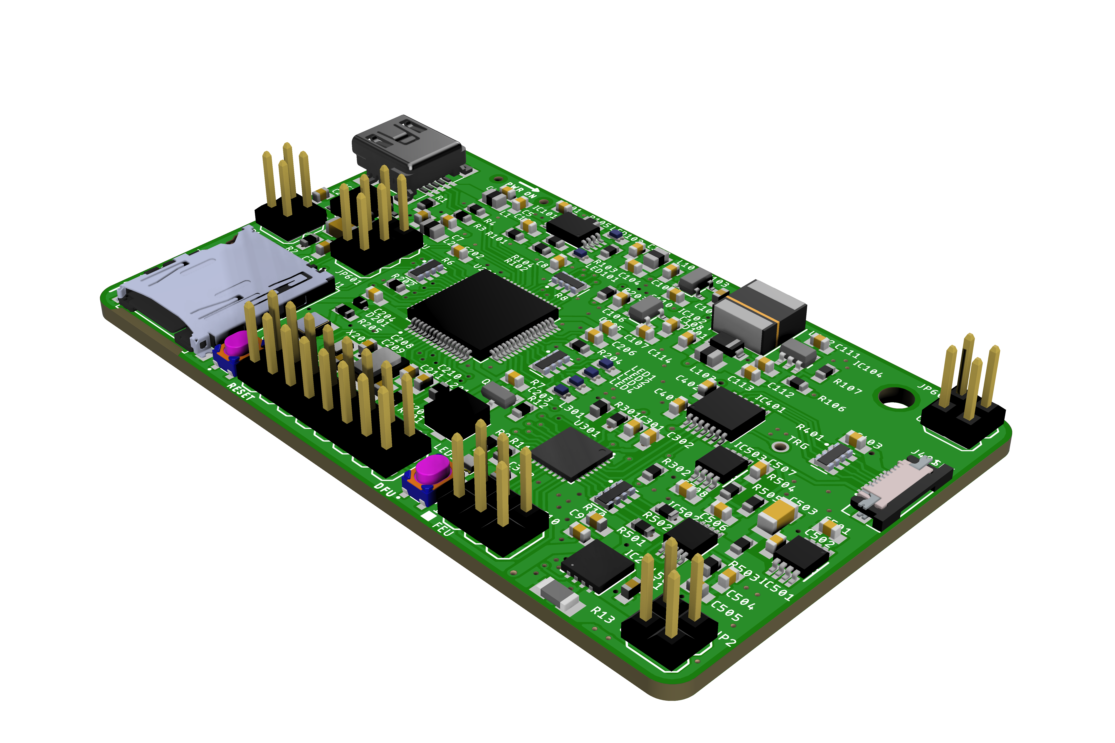
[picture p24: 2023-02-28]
Eagle/chlorophyll_analyzer/chlorophyll_analyzer_rendering.png

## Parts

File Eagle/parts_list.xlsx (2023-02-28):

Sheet: Sheet1
 |  |  |  | セラミックコンデンサ
部品番号 | 品名 | 部品定数 | メーカー | 品番
C211, C212 | セラミックコンデンサ | 50V 12pF | muRata | GRM1882C1H120JA01
C8, C213, C214 | セラミックコンデンサ | 50V 18pF | muRata | GRM1882C1H180JA01
C113 | セラミックコンデンサ | 50V 330pF | muRata | GRM1882C1H331JA01
C506, C507 | セラミックコンデンサ | 50V 2.4nF | muRata | GRM1885C1H242JA01D
C11 | セラミックコンデンサ | 50V 47nF | muRata | GCM188R71H473KA55D
C5, C7, C10, C105, C108, C114, C201, C202, C203, C204, C205, C206, C207, C208, C301, C302, C303, C401, C402, C508 | セラミックコンデンサ | 50V 0.1uF | muRata | CM105W5R103K50VAT
C106, C109, C501, C502, C504, C505 | セラミックコンデンサ | 10V 1uF | muRata | GRM188R6YA106MA73
C207, C219 | セラミックコンデンサ | 10V 4.7uF | muRata | GRM188F11A475ZE20
C3, C4, C9, C101, C102, C103, C104, C107, C110, C111, C112, C403 | セラミックコンデンサ | 10V 22uF | muRata | GRM188R61A226ME
C1, C11, C503 | セラミックコンデンサ | 10V 47uF | muRata | GRM31CB31A476KE15
C210 | セラミックコンデンサ | 3.3V 11mF | Seiko | CPH3225A
CN1 | USB miniB コネクタ | USB miniB | HIROSE | MUSB-5B-NE-S175
D1, D2, D3, D201 | ショットキーバリアダイオード | 30V 200mA | ROHM | RB520S-30
D101 | ショットキーバリアダイオード | 30V 1A | TOSHIBA | CUS10F30 H3F
IC1 | リニアレギュレータ | 5V 1.5A | ROHM | BD50HC5WEFJ-E2
IC2 | リニアLEDドライバ | 500mA 1ch | TI | TL4242DRJR
IC101 | パワーマルチプレクサ | 1.25A 2:1 | TI | TPS2113PW
IC102, IC103 | リニアレギュレータ | 3.3V 100mA | New JRC | NJM2863F33
IC104 | DC/DCスイッチングレギュレータ | ADJ 2.1A | TI | LM2735YQMF
IC501 | リファレンス電源 | 5V 0.1％ | TI | REF5050AIDGKT
IC502 | SAR A/Dコンバータ | 16bit 1ch | TI | ADS8866IDGS
IC503 | 高精度スーパーβオペアンプ | 2ch | TI | OPA2210IDGKT
J1 | MicroSDC コネクタ | micro SDC | HIROSE | DM3AT-SF-PEJM5
JP1, JP2, JP601 JP602, JP603, JP604 | 2列ピンヘッダ | 3A 2.54mm | Usecconn | PH-2x40SG
L1, L2, L101, L103 | フェライトビーズ | 330Ω | muRata | BLM21PG331SN
L201, L301, L501 | フェライトビーズ | 600Ω | muRata | BK2125HS601-T
L102 | パワーインダクタ | 15uH 1.8A | TAIYO | NR6028T150M
LED1, LED3, LED5 | 高輝度LED | Blue | ROHM | SMLE13BC8TT86
LED2, LED4, LED6 | 高輝度LED | Green | ROHM | SML-E12P8WT86
LED101 | LED | Red | OptoSupply | OSHR1608C1A
LED102 | LED | Orange | OptoSupply | OSOR1608C1A
LS1 | トランスデューサ | 3V 90mA | PUI Audio | XDCR_SMT-0440-T-R
Q1 | Nch MOSFET | 50V 300mA | PANJIT | BSS138
R501, R503 | 抵抗器 | 0Ω 1A | KOA | RK73Z1JTTD
R4,R5 | 抵抗器 | 10Ω 1/10W | FAITHFUL LINK | RC0603J10R
R7, R9, R11, R401 | 抵抗器アレイ | 10Ω 1/10W 4ch | Panasonic | EXB-38V100JV
R205 | 抵抗器 | 100Ω 1/10W | FAITHFUL LINK | RC0603J100R
R103 | 薄膜抵抗器 | 402Ω 1/10W | YAGEO | RT0603DRD07402RL
R13,R101 | 抵抗器 | 1kΩ 1/10W | FAITHFUL LINK | RC0603J1K
R8 | 抵抗器アレイ | 4.7kΩ 1/10W 4ch | Panasonic | EXB-38V472JV
R8, R10, R104, R105, R204 | 抵抗器 | 4.7kΩ 1/10W | FAITHFUL LINK | RC0603J4K7
R102, R201, R202, R203, R301, R302 | 抵抗器 | 10kΩ 1/10W | FAITHFUL LINK | RC0603J10K
R107 | 薄膜抵抗器 | 10.2kΩ 1/10W | YAGEO | RT0603DRE0710K2L
R504, R505 | 薄膜抵抗器 | 20kΩ 1/10W | YAGEO | RT0603FRE0720KL
R2 | 抵抗器アレイ | 22kΩ 1/10W 4ch | Panasonic | EXB-38V223JV
R106 | 薄膜抵抗器 | 86.6kΩ 1/10W | YAGEO | RT0603DRD0786K6L
R1, R3, R15, | 抵抗器 | 100kΩ 1/10W | FAITHFUL LINK | RC0603J100K
S1, S2 | タクトスイッチ | 16V 50mA | ALPS | SKRPACE010
S3 | スライドスイッチ | 6V 300mA | C&K | JS102011SAQN
U201 | Arm マイコン | 32bit 512kByte | STMicro | STM32F446RET6
U301 | Arm マイコン | 32bit 256kByte | STMicro | STM32L432KCU6
X201 | 水晶発振子 | 8.00MHz | Kyocera | CX5032GB08000H0HPQZ1
X202 | 水晶発振子 | 32.768kHz | Kyocera | ST3215SB32768H5HPWAA

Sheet: Sheet2
部品番号 | 品名 | 部品定数 | メーカー | 品番
C14, C15 | セラミックコンデンサ | 50V 12pF | muRata | GRM1882C1H120JA01
C1，C9, C10 | セラミックコンデンサ | 50V 0.1uF | muRata | CM105W5R103K50VAT
C4, C6, C7, C8，C11, C16 | セラミックコンデンサ | 10V 1uF | muRata | GRM188R6YA106MA73
C13 | セラミックコンデンサ | 35V 10uF | muRata | GRM188R6YA106MA73
C5 | セラミックコンデンサ | 10V 22uF | muRata | GRM188R61A226ME
C2, C3, C12 | セラミックコンデンサ | 10V 47uF | muRata | GRM31CB31A476KE15
IC1 | リニアレギュレータ | 3.3V 100mA | New JRC | NJM2863F33
IC2 | DMOSシンクドライバ | 7ch 50V 300mA | TOSHIBA | TBD62503AFNG
IC3 | 温度センサ | ₋40C - +105C | Analog Devices | ADT7410TRZ
J1, J6 | FPCコネクタ | 8POS 0.5mm | Wurth Elektronik | 687108183722"
J2, J3, J4, J5 | 2列ピンソケット | 3A 2.54mm | Usecconn | FH-2X25SG
JP1, JP2 | 2列ピンヘッダ | 3A 2.54mm | Usecconn | PH-2x40SG
L1 | インダクタ | 15nH 500mA | Wurth Elektronik | 744786115A
L2 | インダクタ | 10uH 50mA | muRata | LQM18FN100M00D
LED1, LED2 LED3, LED4 | 高輝度LED | Blue | ROHM | SMLE13BC8TT86
LED5, LED6 | LED | Red | OptoSupply | OSHR1608C1A
M1 | キャラクタLCD | White | Xiamen | AQM1602Y-NLW-FBW
M2 | 無線モジュール | nRF52832 SoC | RAYTAC | MDBT42Q-512KV2
Q1, Q2, Q3, Q4 | Nch MOSFET | 50V 300mA | PANJIT | BSS138
R1, R2, R3, R4, R12 | 抵抗器 | 1kΩ 1/10W | FAITHFUL LINK | RC0603J1K
R5, R6, R7, R8, R9 | 抵抗器 | 4.7kΩ 1/10W | FAITHFUL LINK | RC0603J4K7
R10, R11, R13, R14, R16 | 抵抗器 | 10kΩ 1/10W | FAITHFUL LINK | RC0603J10K
R15 | 抵抗器アレイ | 4.7kΩ 1/10W 4ch | Panasonic | EXB-38V472JV
S1, S2, S3, S4 | タクトスイッチ |  | Cosland | DTS-6-V
S5 | タクトスイッチ |  | ALPS | SKRPACE010

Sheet: Sheet3
部品番号 | 品名 | 部品定数 | メーカー | 品番
C1, C3 | セラミックコンデンサ | 10V 22uF | muRata | GRM188R61A226ME
C2 | セラミックコンデンサ | 50V 0.1uF | muRata | CM105W5R103K50VAT
J1 | FPCコネクタ | 8POS 0.5mm | Wurth Elektronik | 687108183722"
L1 | フェライトビーズ | 330Ω | muRata | BLM21PG331SN
M1 | マイクロ分光器 | 340~850nm | Hamamatsu | C12880MA
R1 | 抵抗器アレイ | 4.7kΩ 1/10W 4ch | Panasonic | EXB-38V472JV

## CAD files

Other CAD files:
Fusion/chlorophyll_analizer_extra.f3d
Fusion/chlorophyll_analyzer_LEDs.f3d
Fusion/chlorophyll_analyzer_attachment.f3d
Fusion/chlorophyll_analyzer_spectorometer.f3d

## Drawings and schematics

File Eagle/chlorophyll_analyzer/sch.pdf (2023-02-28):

A

A

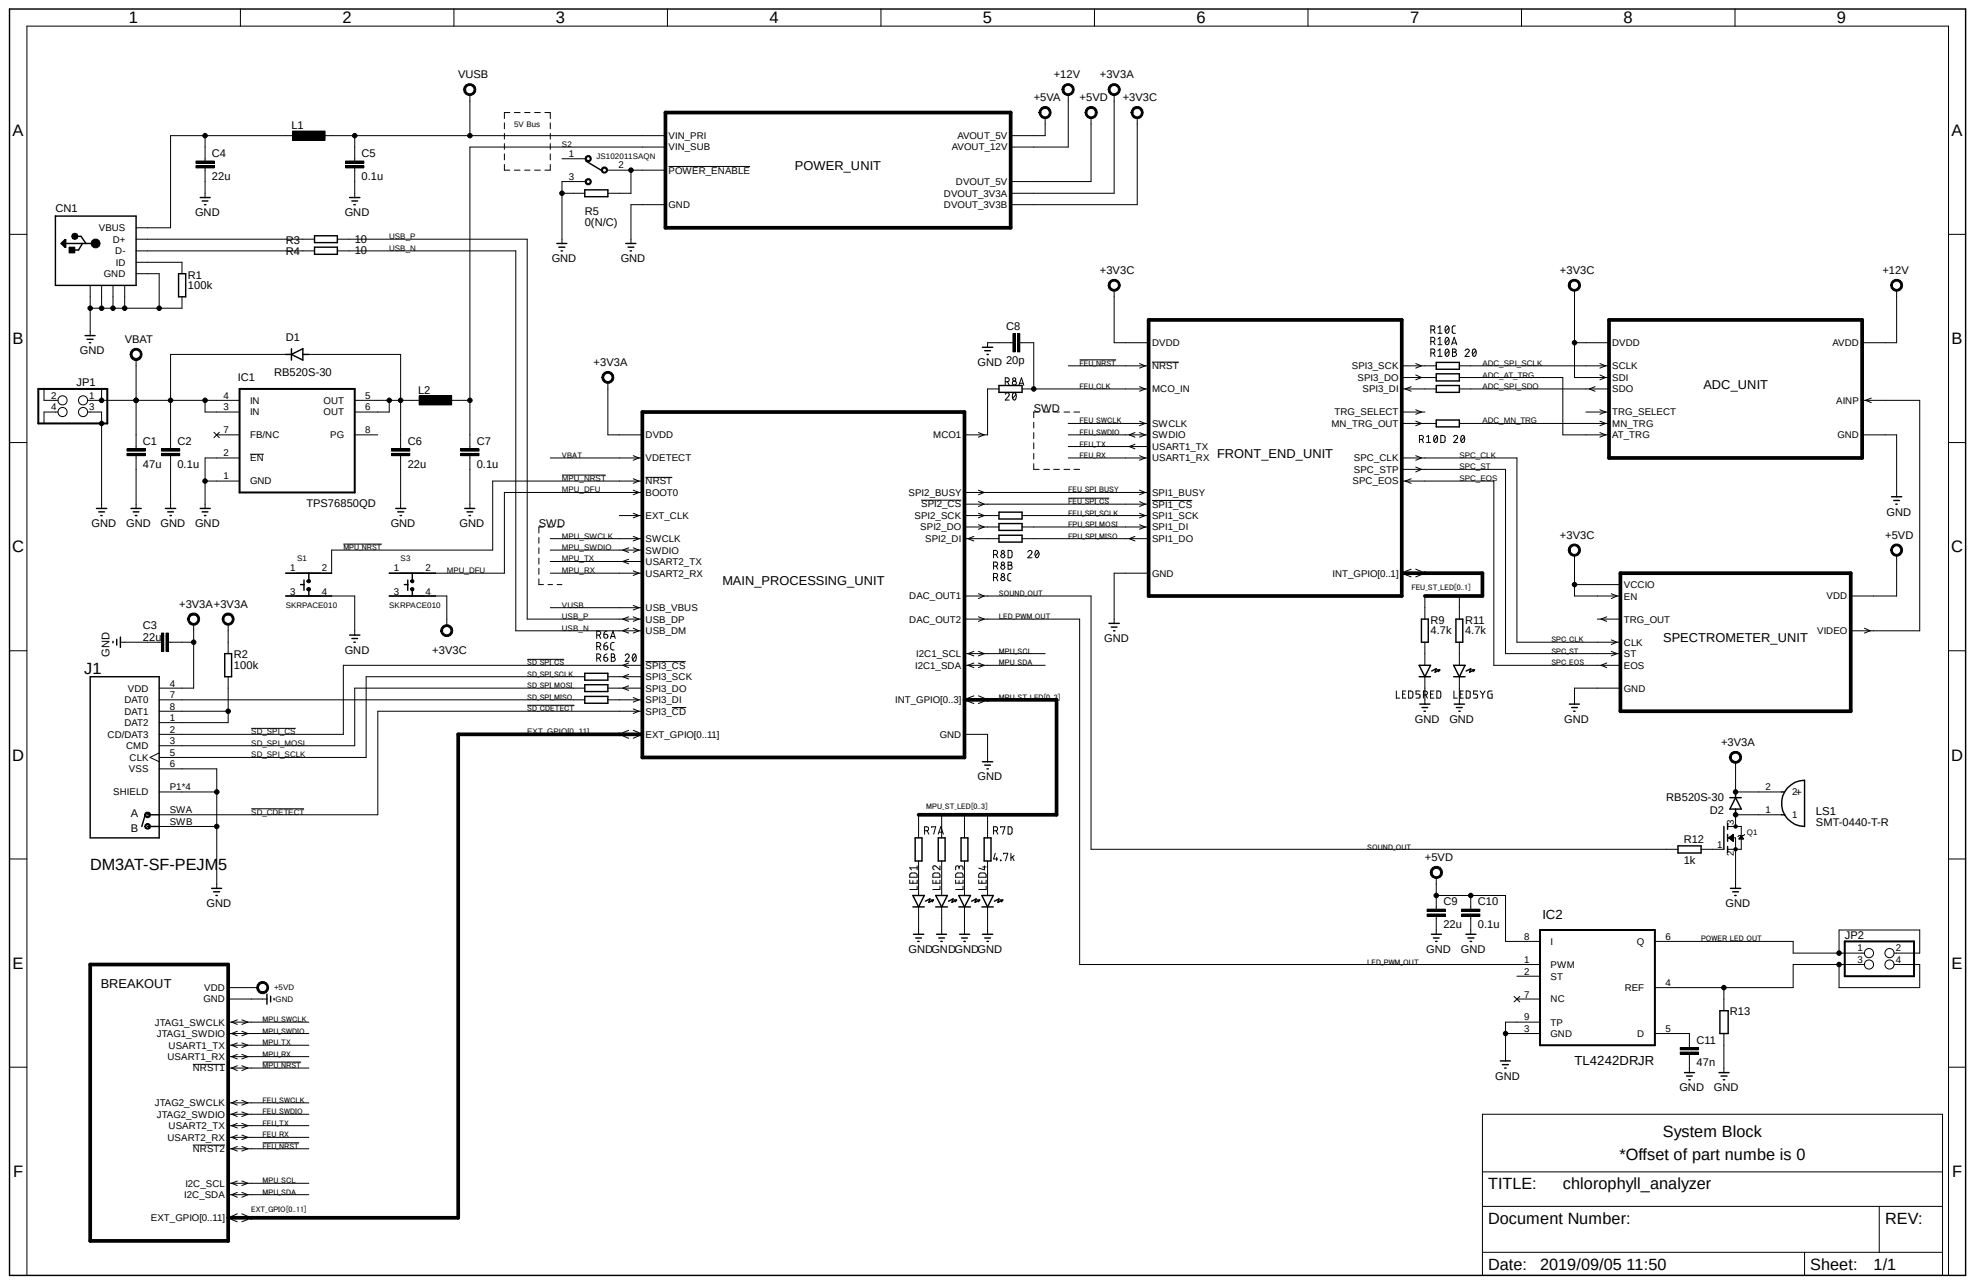
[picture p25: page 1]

System Block
*Offset of part numbe is 0

Document Number: | REV:

Date: 2019/09/05 11:50 | Sheet: 1/1

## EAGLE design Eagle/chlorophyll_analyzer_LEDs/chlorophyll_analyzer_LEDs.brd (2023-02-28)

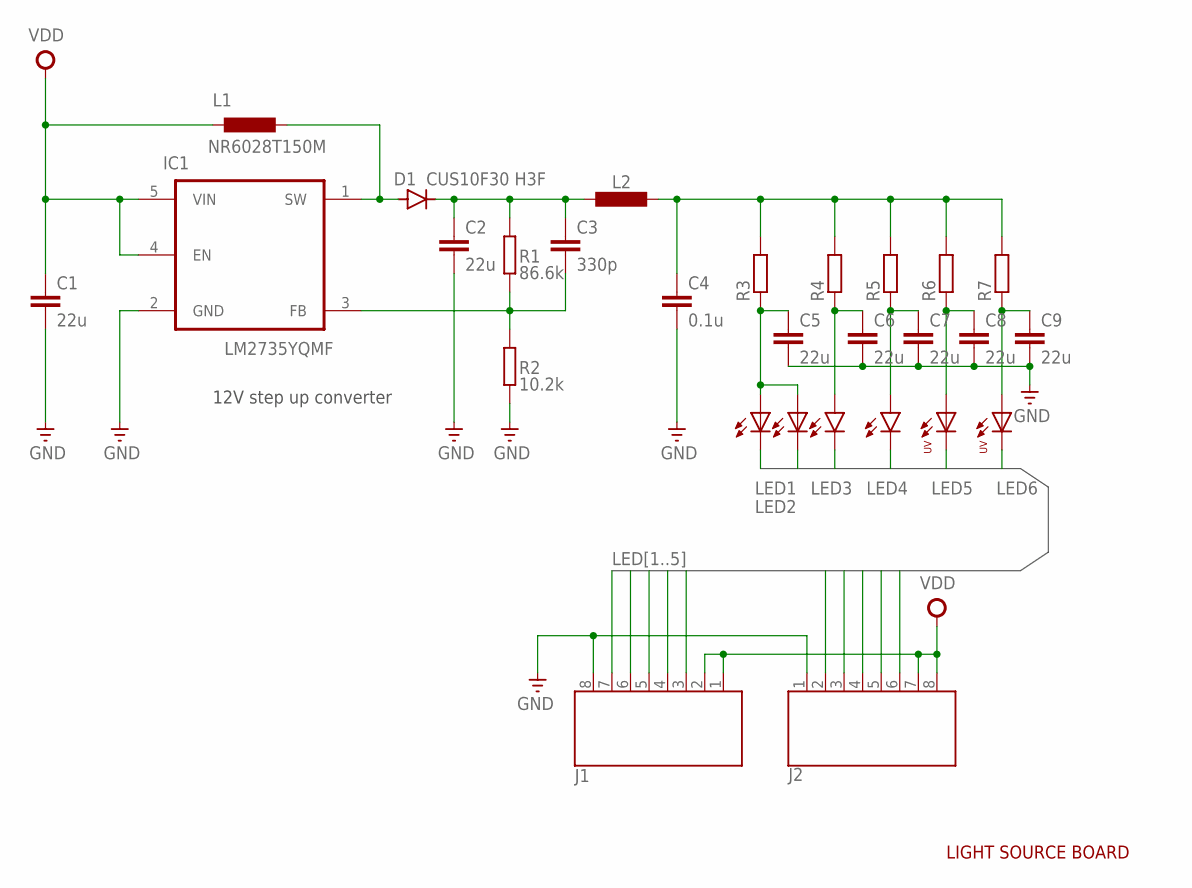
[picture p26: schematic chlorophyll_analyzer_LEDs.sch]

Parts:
C1, C2, C5, C6, C7, C8, C9: 22u; C0603K
C3: 330p; C0603K
C4: 0.1u; C0603K
D1: CUS10F30 H3F; SOD323-W
IC1: LM2735YQMF; SOT65P285X120-5N
J1, J2: 687108183722
L1: NR6028T150M; IND_TAIYO_NR6028
L2: INDUCOR2012; SMD2012
LED1, LED2: L130-S1S0-3030509506-0000003S-000015080003000W21; LED_L130-5080003000W21
LED3, LED4: LEDCHIPLED_1206; CHIPLED_1206
LED5, LED6: ELUA2016OGB-P8090Q53038020-VA1M; ELUA2016OGB0.08
R1: 86.6k; SMD1608
R2: 10.2k; SMD1608
R3, R4, R5, R6, R7: R-EU_R0805; R0805

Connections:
AVOUT_12V: C4.1, L2.1, R3.2, R4.2, R5.2, R6.2, R7.2
GND: C1.2, C2.2, C4.2, C5.2, C6.2, C7.2, C8.2, C9.2, IC1.2 (GND), J1.8 (1), J2.1 (8), R2.1
LED1: J1.3 (6), J2.6 (3), LED1.C, LED2.C
LED2: J1.4 (5), J2.5 (4), LED3.C
LED3: J1.5 (4), LED4.C
LED4: J1.6 (3), J2.3 (6), J2.4 (5), LED5.C (C1)
LED5: J1.7 (2), J2.2 (7), LED6.C (C1)
unnamed: C5.1, LED1.A, LED2.A, R3.1
unnamed: C6.1, LED3.A, R4.1
unnamed: C7.1, LED4.A, R5.1
unnamed: C9.1, LED6.A (A1), R7.1
unnamed: C8.1, LED5.A (A1), R6.1
unnamed: C2.1, C3.1, D1.C, L2.2, R1.2
unnamed: D1.A, IC1.1 (SW), L1.1
unnamed: C3.2, IC1.3 (FB), R1.1, R2.2
VDD: C1.1, IC1.4 (EN), IC1.5 (VIN), J1.1 (8), J1.2 (7), J2.7 (2), J2.8 (1), L1.2

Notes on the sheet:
12V step up converter
LIGHT SOURCE BOARD

Board: 2 copper layers, 28 parts (21 on the bottom side), 16 nets, no tracks yet.

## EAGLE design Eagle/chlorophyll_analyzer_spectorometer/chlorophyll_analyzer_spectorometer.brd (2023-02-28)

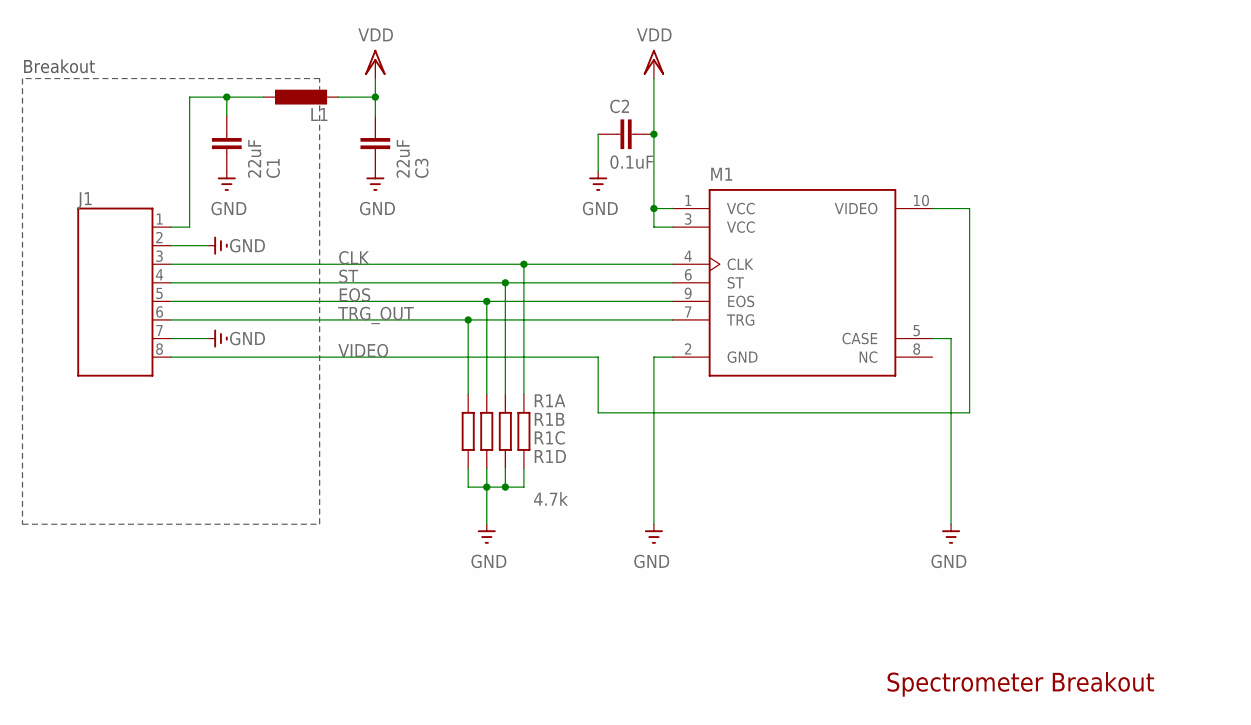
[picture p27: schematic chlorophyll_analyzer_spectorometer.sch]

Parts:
C1, C3: 22uF; C0603K
C2: 0.1uF; C0603K
J1: 687108183722
L1: INDUCOR1608; SMD1608
M1: C12880MA
R1: 4.7k; RESCAXS80P320X160X60-8N

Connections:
CLK: J1.3 (6), M1.4 (CLK), R1.5 (2)
EOS: J1.5 (4), M1.9 (EOS), R1.7 (2)
GND: C1.2, C2.2, C3.2, J1.2 (7), J1.7 (2), M1.2 (GND), M1.5 (CASE), R1.1, R1.2 (1), R1.3 (1), R1.4 (1)
unnamed: C1.1, J1.1 (8), L1.1
ST: J1.4 (5), M1.6 (ST), R1.6 (2)
TRG_OUT: J1.6 (3), M1.7 (TRG), R1.8 (2)
VDD: C2.1, C3.1, L1.2, M1.1 (VCC), M1.3 (VCC)
VIDEO: J1.8 (1), M1.10 (VIDEO)

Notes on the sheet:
Breakout
Spectrometer Breakout

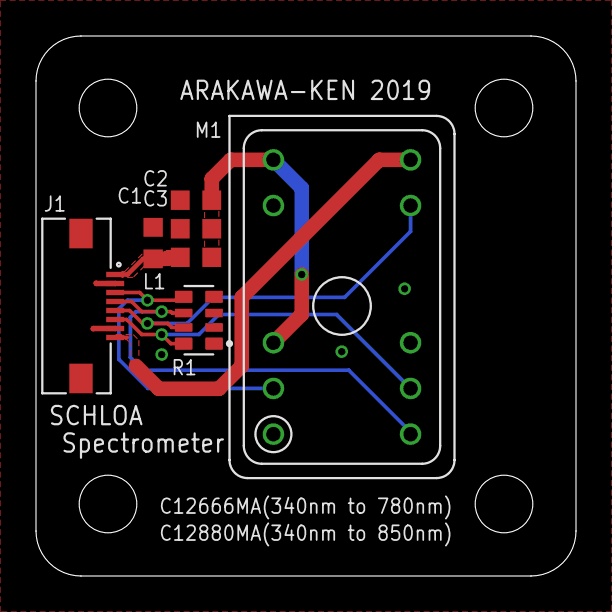
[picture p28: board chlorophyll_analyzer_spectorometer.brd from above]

Board: 2 copper layers, 30.0 x 30.0 mm, 7 parts (0 on the bottom side), 8 nets.

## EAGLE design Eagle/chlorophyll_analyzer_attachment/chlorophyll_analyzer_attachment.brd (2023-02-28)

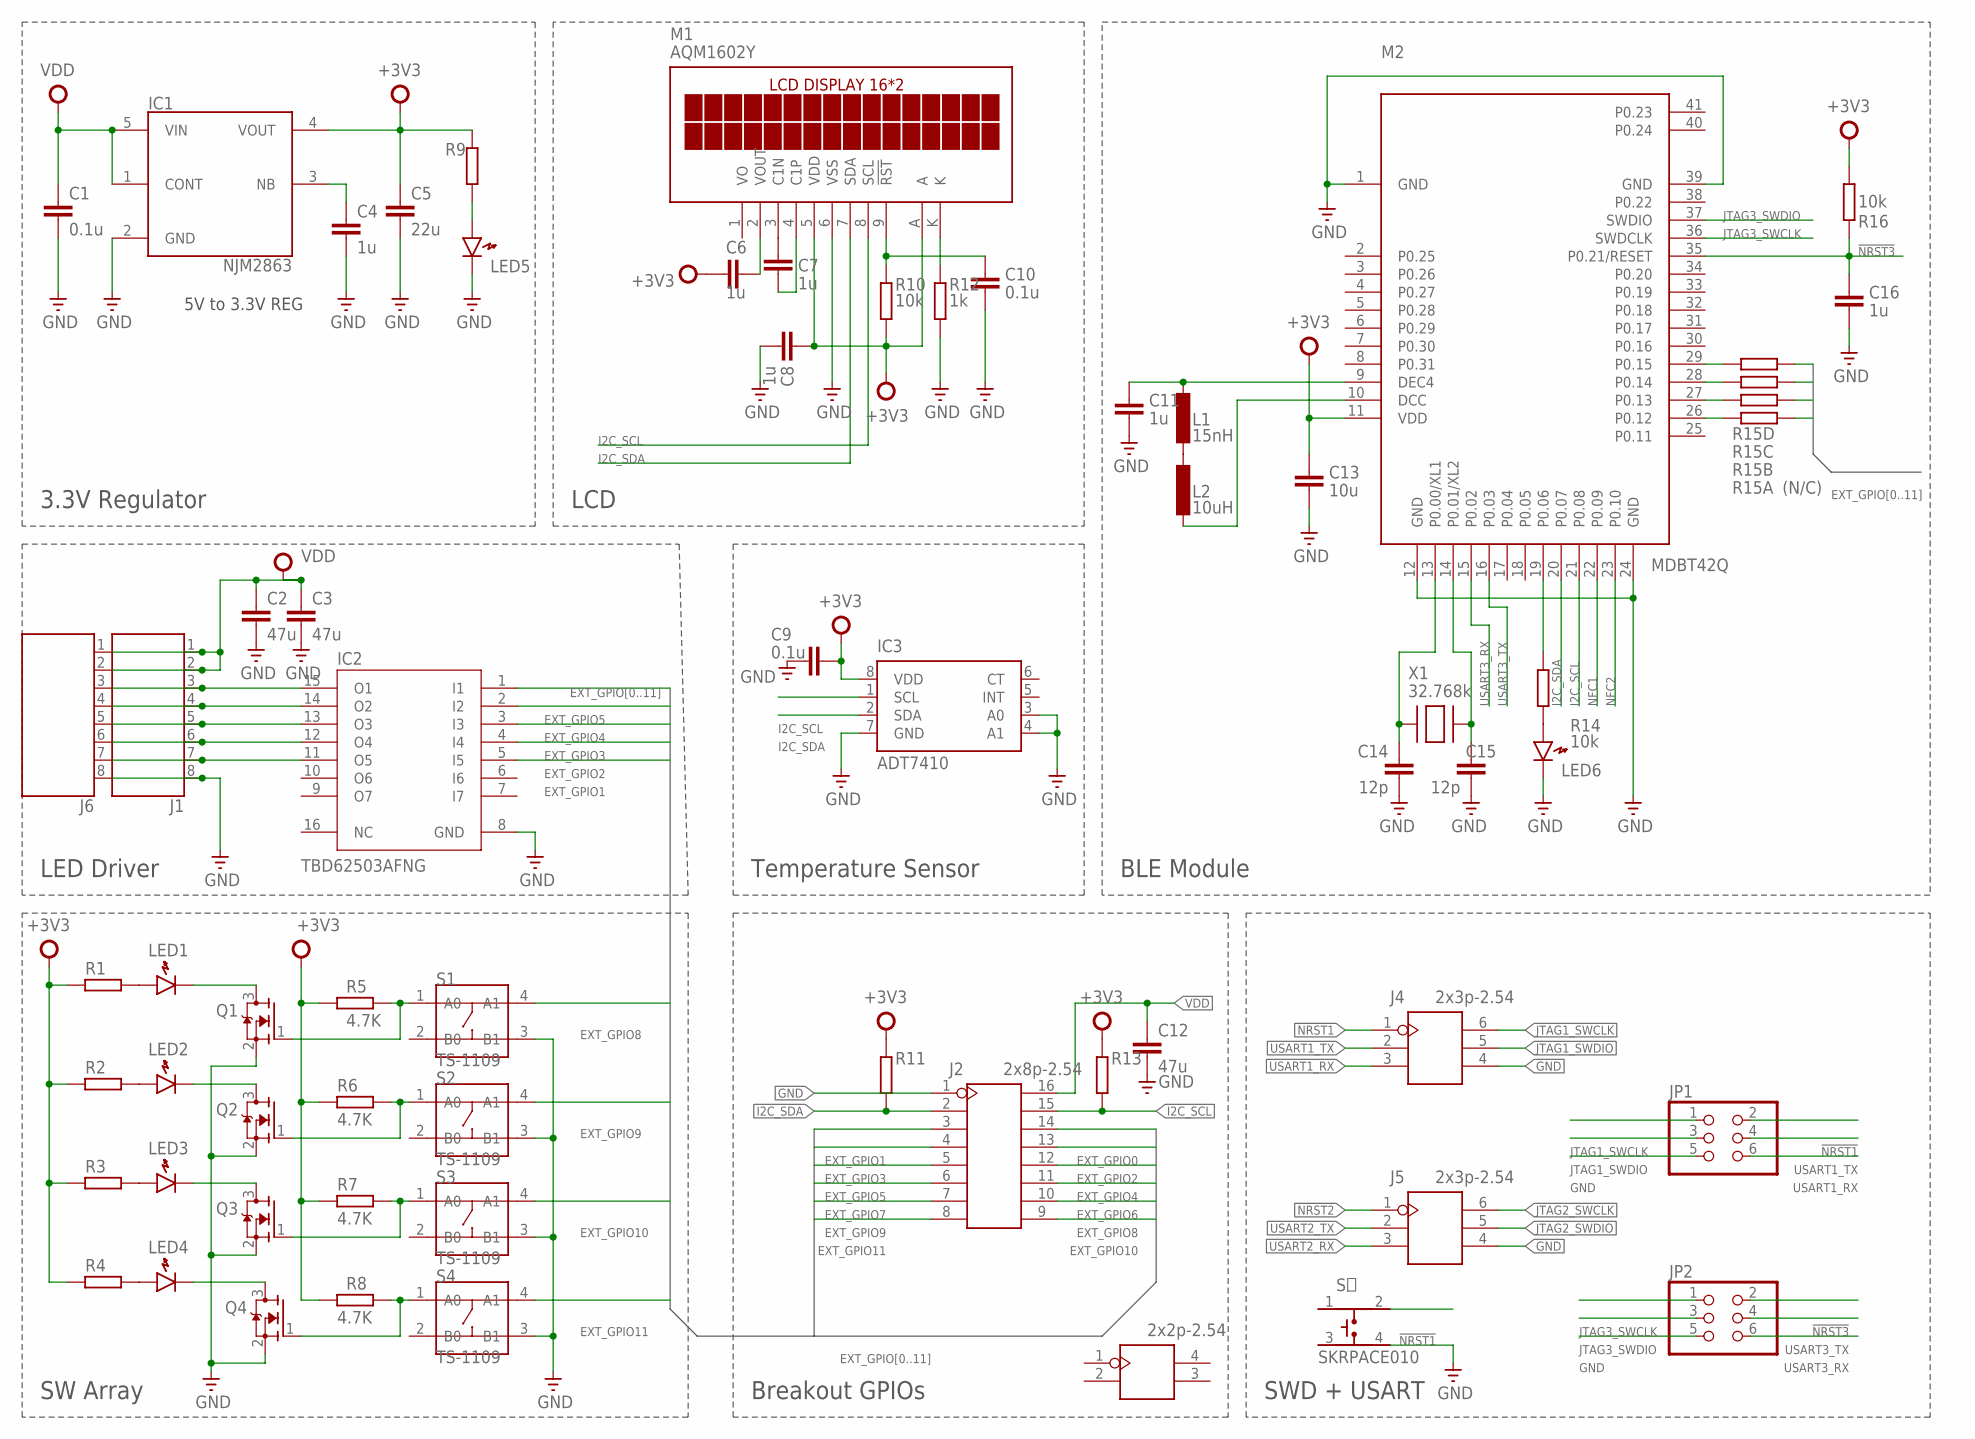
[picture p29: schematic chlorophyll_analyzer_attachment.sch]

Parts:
C1, C9, C10: 0.1u; C0603K
C2, C3, C12: 47u; C1206
C4, C6, C7, C8, C11, C16: 1u; C0603K
C5: 22u; C0603K
C13: 10u; C0603K
C14, C15: 12p; C0603K
IC1: NJM2863; SOT-23-5
IC2: TBD62503AFNG; SSOP16-P-225-0.65B
IC3: ADT7410; SOIC8
J1, J6: 687108183722
J2: 2x8p-2.54; H2X8-2.54
J3: 2x2p-2.54; H2X2-2.54
J4, J5: 2x3p-2.54; H2X3-2.54
JP1, JP2: PINHD-2X3; 2X03
L1: 15nH; SMD1608
L2: 10uH; SMD1608
LED1, LED2, LED3, LED4, LED5, LED6: LED1608
M1: AQM1602Y
M2: MDBT42Q
Q1, Q2, Q3, Q4: MOSFET-NREFLOW; SOT23
R1, R2, R3, R4, R9, R11, R13: RESISTOR1608; SMD1608
R5, R6, R7, R8: 4.7K; SMD1608
R10, R14, R16: 10k; SMD1608
R12: 1k; SMD1608
R15: (N/C); RESCAXS80P320X160X60-8N
S1, S2, S3, S4: TS-1109; SW4-6.0X6.0X5.0MM
S５: SKRPACE010; SW_SKRPACE010
X1: 32.768k; XTAL3215

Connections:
!NRST1: J4.1, JP1.2, S５.2
!NRST2: J5.1
!NRST3: C16.1, JP2.2, M2.35 (P0.21/RESET), R16.1
+3V3: C5.1, C6.1, C8.2, C9.1, C13.1, IC1.4 (VOUT), IC3.8 (VDD), M1.5 (VDD), M1.A, M2.11 (VDD), R1.1, R2.1, R3.1, R4.1, R5.1, R6.1, R7.1, R8.1, R9.1, R10.2, R11.1, R13.1, R16.2
EXT_GPIO0: J2.14
EXT_GPIO1: IC2.5 (I5), J2.3
EXT_GPIO2: IC2.4 (I4), J2.13
EXT_GPIO3: IC2.3 (I3), J2.4
EXT_GPIO4: IC2.2 (I2), J2.12
EXT_GPIO5: IC2.1 (I1), J2.5
EXT_GPIO6: J2.11
EXT_GPIO7: J2.6
EXT_GPIO8: J2.10, R15.8 (2), S1.4 (A1)
EXT_GPIO9: J2.7, R15.7 (2), S2.4 (A1)
EXT_GPIO10: J2.9, R15.6 (2), S3.4 (A1)
EXT_GPIO11: J2.8, R15.5 (2), S4.4 (A1)
GND: C1.2, C2.2, C3.2, C4.2, C5.2, C8.1, C9.2, C10.2, C11.2, C12.2, C13.2, C14.2, C15.2, C16.2, IC1.2 (GND), IC2.8 (GND), IC3.3 (A0), IC3.4 (A1), IC3.7 (GND), J1.8 (1), J2.1, J4.4, J5.4, J6.8 (1), JP1.5, JP2.5, LED5.K, LED6.K, M1.6 (VSS), M2.1 (GND), M2.12 (GND), M2.24 (GND), M2.39 (GND), Q1.2 (S), Q2.2 (S), Q3.2 (S), Q4.2 (S), R12.2, S1.3 (B1), S2.3 (B1), S3.3 (B1), S4.3 (B1), S５.4
I2C_SCL: IC3.1 (SCL), J2.15, M1.8 (SCL), M2.21 (P0.08), R13.2
I2C_SDA: IC3.2 (SDA), J2.2, M1.7 (SDA), M2.20 (P0.07), R11.2
JTAG1_SWCLK: J4.6, JP1.1
JTAG1_SWDIO: J4.5, JP1.3
JTAG2_SWCLK: J5.6
JTAG2_SWDIO: J5.5
JTAG3_SWCLK: JP2.1, M2.36 (SWDCLK)
JTAG3_SWDIO: JP2.3, M2.37 (SWDIO)
unnamed: C6.2, M1.2 (VOUT)
unnamed: C7.2, M1.3 (C1N)
unnamed: C7.1, M1.4 (C1P)
unnamed: C4.1, IC1.3 (NB)
unnamed: LED5.A, R9.2
unnamed: C10.1, M1.9 (!RST), R10.1
unnamed: M1.K, R12.1
unnamed: Q1.1 (G), R5.2, S1.1 (A0)
unnamed: Q2.1 (G), R6.2, S2.1 (A0)
unnamed: Q3.1 (G), R7.2, S3.1 (A0)
unnamed: Q4.1 (G), R8.2, S4.1 (A0)
unnamed: L2.2, M2.10 (DCC)
unnamed: M2.19 (P0.06), R14.2
unnamed: C11.1, L1.1, M2.9 (DEC4)
unnamed: LED6.A, R14.1
unnamed: LED1.A, R1.2
unnamed: LED2.A, R2.2
unnamed: LED3.A, R3.2
unnamed: LED4.A, R4.2
unnamed: LED4.K, Q4.3 (D)
unnamed: LED3.K, Q3.3 (D)
unnamed: LED2.K, Q2.3 (D)
unnamed: LED1.K, Q1.3 (D)
unnamed: C14.1, M2.13 (P0.00/XL1), X1.P$1
unnamed: L1.2, L2.1
unnamed: C15.1, M2.14 (P0.01/XL2), X1.P$2
unnamed: M2.26 (P0.12), R15.1
unnamed: M2.27 (P0.13), R15.2 (1)
unnamed: M2.28 (P0.14), R15.3 (1)
unnamed: M2.29 (P0.15), R15.4 (1)
unnamed: IC2.15 (O1), J1.3 (6), J6.3 (6)
unnamed: IC2.14 (O2), J1.4 (5), J6.4 (5)
unnamed: IC2.13 (O3), J1.5 (4), J6.5 (4)
unnamed: IC2.12 (O4), J1.6 (3), J6.6 (3)
unnamed: IC2.11 (O5), J1.7 (2), J6.7 (2)
NFC1: M2.22 (P0.09)
NFC2: M2.23 (P0.10)
USART1_RX: J4.3, JP1.6
USART1_TX: J4.2, JP1.4
USART2_RX: J5.3
USART2_TX: J5.2
USART3_RX: JP2.6, M2.15 (P0.02)
USART3_TX: JP2.4, M2.16 (P0.03)
VDD: C1.1, C2.1, C3.1, C12.1, IC1.1 (CONT), IC1.5 (VIN), J1.1 (8), J1.2 (7), J2.16, J6.1 (8), J6.2 (7)

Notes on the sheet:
SWD + USART
Breakout GPIOs
5V to 3.3V REG
SW Array
LED Driver
Temperature Sensor
BLE Module
3.3V Regulator
LCD

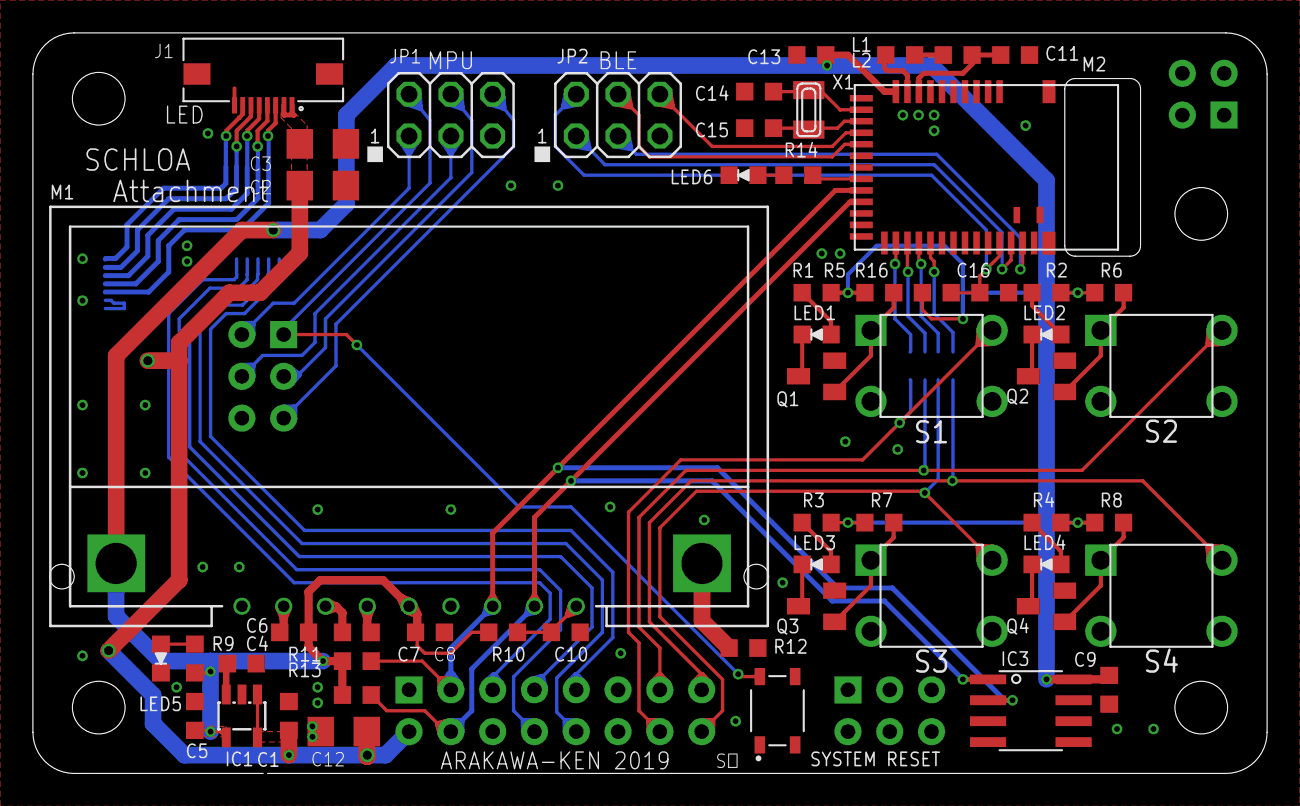
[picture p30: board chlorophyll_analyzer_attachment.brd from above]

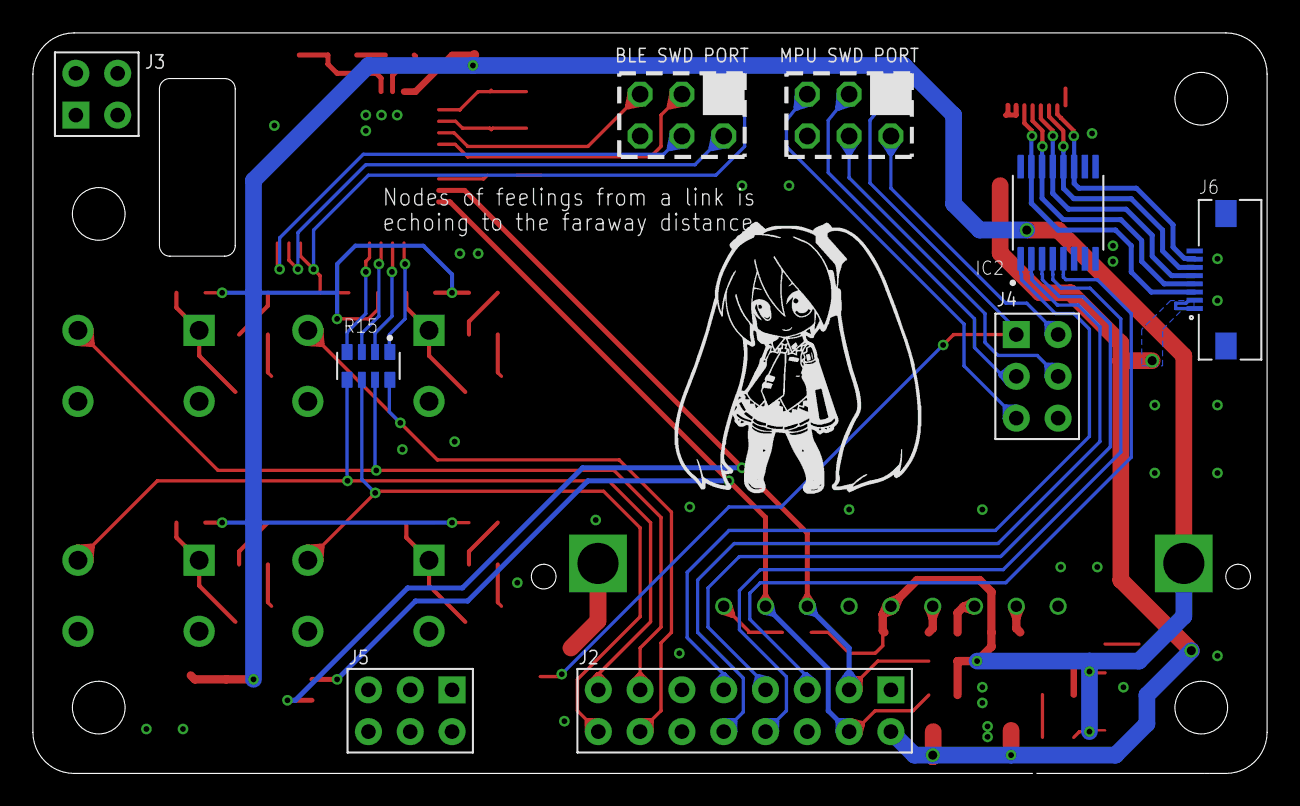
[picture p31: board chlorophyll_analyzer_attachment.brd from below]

Board: 2 copper layers, 75.0 x 45.0 mm, 63 parts (7 on the bottom side), 59 nets.

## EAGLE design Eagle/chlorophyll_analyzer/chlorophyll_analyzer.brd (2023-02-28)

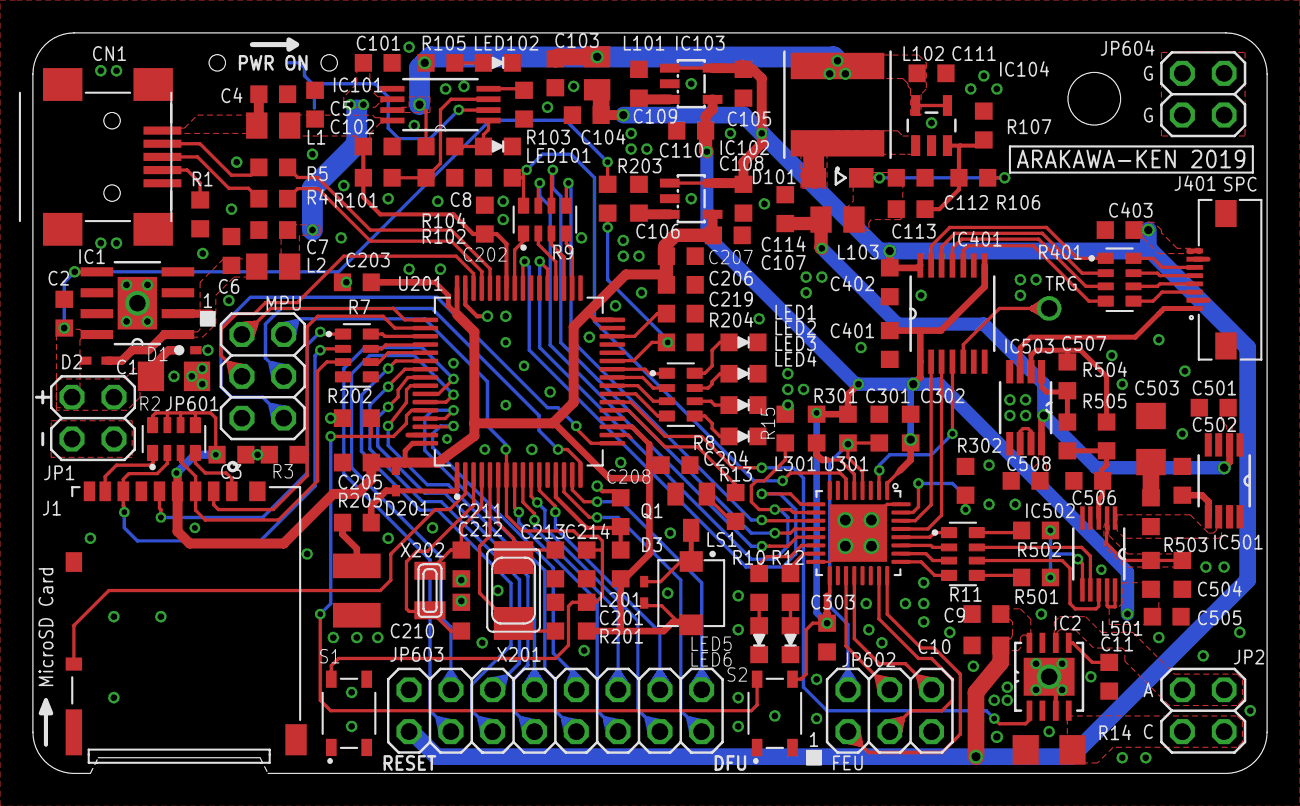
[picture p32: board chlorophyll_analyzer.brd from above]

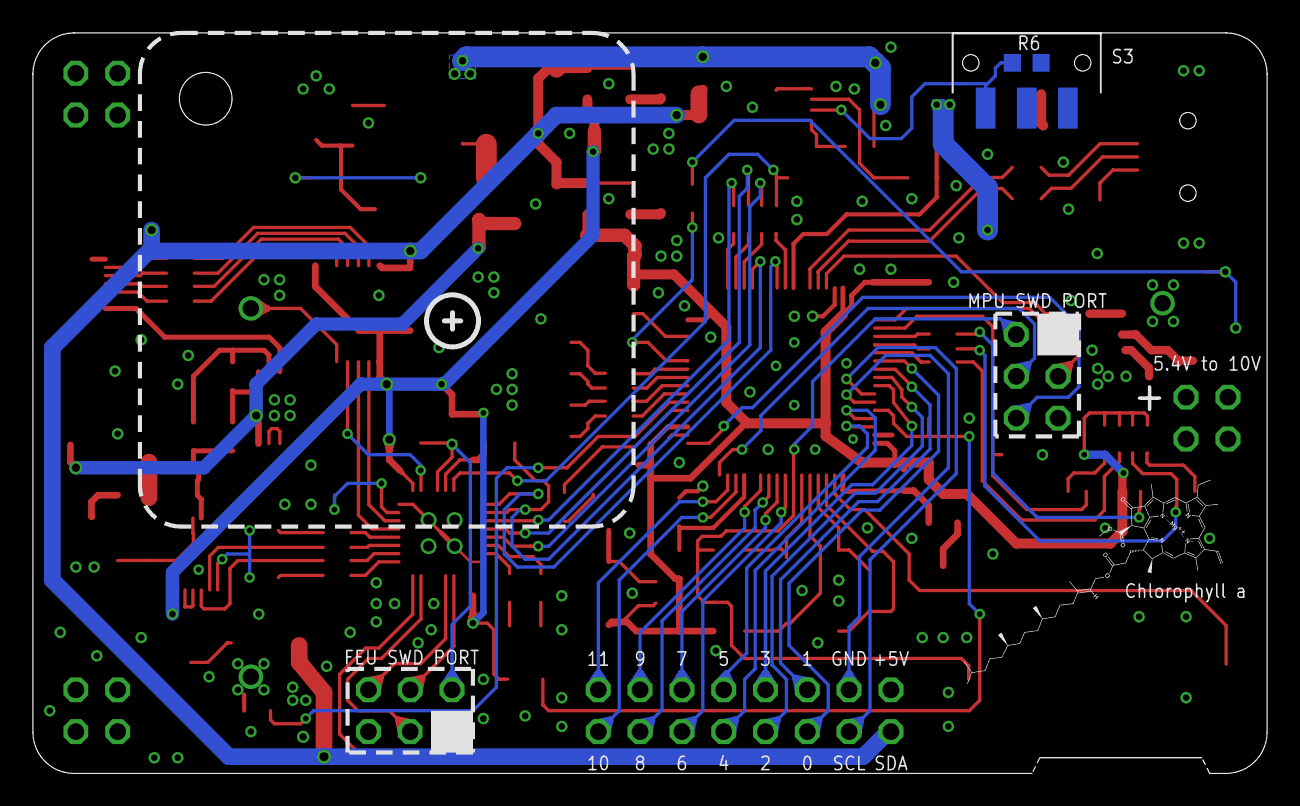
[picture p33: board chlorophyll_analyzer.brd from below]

Board: 2 copper layers, 75.0 x 45.0 mm, 137 parts (2 on the bottom side), 130 nets.

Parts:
C1, C503: 47u; C1206
C2, C106, C109, C501, C502, C504, C505: 1u; C0603K
C3, C4, C6, C9, C101, C102, C103, C104, C107, C110, C111, C112: 22u; C0603K
C5, C7, C10, C105, C108, C114, C201, C202, C203, C204, C205, C206, C208, C301, C302, C303, C401, C402, C508: 0.1u; C0603K
C8: 20p; C0603K
C11: 47n; C0603K
C113: 330p; C0603K
C207, C219: 4.7u; C0603K
C210: CPH3225A(11mF); C1210K
C211, C212: 12p; C0603K
C213, C214: 18p; C0603K
C403: 22uF; C0603K
C506, C507: 2.4n; C0603K
CN1: USB-MINIB
D1, D2, D3, D201: RB520S-30; SOD523
D101: CUS10F30 H3F; SOD323-W
IC1: BD50HC5WEFJ; HTSOP-J8
IC2: TL4242DRJR; SON80P410X410X80-9N
IC101: TPS2113PW; SOP65P640X120-8N
IC102, IC103: NJM2863; SOT-23-5
IC104: LM2735YQMF; SOT65P285X120-5N
IC401: TXB0104PWR; SOP65P640X120-14N
IC501: REF5050AIDGKT; SOP65P490X110-8N
IC502: ADS8866IDGS; SOP50P490X110-10N
IC503: OPA2388IDGKT; SOP65P490X110-9N
J1: DM3AT-SF-PEJM5; HRS_DM3AT-SF-PEJM5
J401: 687108183722
JP1, JP2, JP604: 2X02
JP601, JP602: 2X03
JP603: 2X08
L1, L2, L101, L103: SMD2012
L102: NR6028T150M; IND_TAIYO_NR6028
L201, L301, L501: SMD1608
LED1, LED2, LED3, LED4, LED5, LED6, LED101, LED102: LED1608
LS1: SMT-0440-T-R; XDCR_SMT-0440-T-R
Q1: SOT23
R1, R3, R15: 100k; SMD1608
R2: 22k; RESCAXS80P320X160X60-8N
R4, R5: 10; SMD1608
R6, R502: 0(N/C); SMD1608
R7, R9, R11, R401: 20; RESCAXS80P320X160X60-8N
R8: 4.7k; RESCAXS80P320X160X60-8N
R10, R12, R104, R105, R204: 4.7k; SMD1608
R13, R101: 1k; SMD1608
R14: R1206
R102, R201, R202, R203, R301, R302: 10k; SMD1608
R103: 400; SMD1608
R106: 86.6k; SMD1608
R107: 10.2k; SMD1608
R205: 100; SMD1608
R501, R503: 0; SMD1608
R504, R505: 20k; SMD1608
S1, S2: SKRPACE010; SW_SKRPACE010
S3: JS102011SAQN; SW_JS102011SAQN
U201: STM32F446RET6; QFP50P1200X1200X160-64N
U301: STM32L432KCU6; QFN50P500X500X60-33N
X201: 8.0MHz; NX5032
X202: 32.768k; XTAL3215

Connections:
!FEU_NRST: C301.1, JP602.2, R301.2, U301.4
!FEU_SPI_CS: R15.1, U201.37, U301.10
!MPU_NRST: C201.2, JP601.2, R201.2, S1.2, U201.7
!SD_CDETECT: J1.SWA, U201.2
!SD_SPI_CS: J1.2, R3.1, U201.50
+3V3A: C3.1, C107.1, C203.1, C204.1, C205.1, C206.1, C207.1, D3.C, D201.A, IC102.4, J1.4, L201.1, LS1.2, R2.5, R2.6, R2.7, R2.8, R201.1, U201.19, U201.32, U201.48, U201.64
+3V3C: C110.1, C302.1, C303.1, C401.2, C505.1, IC103.4, IC401.1, IC401.8, IC502.9, IC502.10, L301.1, L501.1, R301.1, S2.4, U301.1, U301.17
+5VA: C103.1, C111.1, IC101.7, IC104.4, IC104.5, L101.2, L102.2, R104.1, R105.1
+5VD: C9.2, C10.2, C104.1, C105.1, C108.1, C402.1, C403.1, IC2.8, IC102.1, IC102.5, IC103.1, IC103.5, IC401.14, J401.8, JP603.1, L101.1
+12V: C114.1, C501.1, C508.1, IC501.2, IC503.8, L103.1
ADC_AT_TRG: R11.8, R502.1
ADC_MN_TRG: R11.5, R501.1
ADC_SPI_MISO: IC502.7, R11.7
ADC_SPI_SCLK: IC502.8, R11.6
ADC_UNIT:ADC_CTRG: IC502.6, R501.2, R502.2
ADC_UNIT:N$1: C503.2, R503.1
ADC_UNIT:N$2: IC503.6, IC503.7
ADC_UNIT:N$3: C504.1, IC502.2, L501.2
ADC_UNIT:N$25: C506.1, IC502.3, R504.1, R505.1
ADC_UNIT:N$26: C507.1, IC503.1, R504.2
ADC_UNIT:N$30: C507.2, IC503.2, R505.2
ADC_UNIT:N$34: C502.1, IC501.5
ADC_UNIT:VREF: IC501.6, IC502.1, R503.2
EXT_GPIO0: JP603.5, U201.54
EXT_GPIO1: JP603.6, U201.55
EXT_GPIO2: JP603.7, U201.56
EXT_GPIO3: JP603.8, U201.57
EXT_GPIO4: JP603.9, U201.61
EXT_GPIO5: JP603.10, U201.62
EXT_GPIO6: JP603.11, U201.8
EXT_GPIO7: JP603.12, U201.9
EXT_GPIO8: JP603.13, U201.10
EXT_GPIO9: JP603.14, U201.11
EXT_GPIO10: JP603.15, U201.14
EXT_GPIO11: JP603.16, U201.15
FEU_MCLK: C8.1, R9.8, U301.6
FEU_RX: JP602.6, U301.20
FEU_SPI_BUSY: U201.40, U301.9
FEU_SPI_SCLK: R9.5, U301.11
FEU_ST_LED0: R10.1, U301.14
FEU_ST_LED1: R12.1, U301.15
FEU_SWCLK: JP602.1, U301.24
FEU_SWDIO: JP602.3, U301.23
FEU_TX: JP602.4, U301.19
FPU_SPI_MISO: R9.6, U301.12
FPU_SPI_MOSI: R9.7, U301.13
FRONT_END_UNIT:N$1: L301.2, U301.5
FRONT_END_UNIT:N$10: R302.1, U301.31
GND: C1.2, C2.2, C3.2, C4.2, C5.2, C6.2, C7.2, C8.2, C9.1, C10.1, C11.1, C101.2, C102.2, C103.2, C104.2, C105.2, C106.2, C107.2, C108.2, C109.2, C110.2, C111.2, C112.2, C114.2, C201.1, C202.1, C203.2, C204.2, C205.2, C206.2, C207.2, C208.2, C210.2, C211.2, C212.2, C213.2, C214.2, C219.2, C301.2, C302.2, C303.2, C401.1, C402.2, C403.2, C501.2, C502.2, C503.1, C504.2, C505.2, C506.2, C508.2, CN1.GND, CN1.GND1, CN1.GND2, CN1.GND3, CN1.GND4, D1.A, IC1.3, IC1.4, IC1.6, IC1.7, IC1.9, IC2.3, IC2.9, IC101.5, IC102.2, IC103.2, IC104.2, IC401.7, IC501.4, IC502.4, IC502.5, IC503.4, IC503.5, J1.6, J1.P1, J1.P2, J1.P3, J1.P4, J1.SWB, J401.2, J401.7, JP1.3, JP1.4, JP601.5, JP602.5, JP603.2, JP604.1, JP604.2, JP604.3, JP604.4, LED1.K, LED2.K, LED3.K, LED4.K, LED5.K, LED6.K, LED101.K, LED102.K, Q1.2, R1.2, R3.2, R6.1, R14.1, R15.2, R102.2, R103.2, R107.1, R202.1, R204.1, R302.2, S1.4, S3.2, U201.12, U201.18, U201.31, U201.47, U201.63, U301.16, U301.32, U301.33
LED_PWM_OUT: IC2.1, U201.22
MAIN_PROCESSING_UNIT:EXT_CLK: C214.1, U201.5, X201.P$1
MAIN_PROCESSING_UNIT:N$1: C219.1, U201.30
MAIN_PROCESSING_UNIT:N$2: C212.1, U201.3, X202.P$2
MAIN_PROCESSING_UNIT:N$3: C208.1, L201.2, U201.13
MAIN_PROCESSING_UNIT:N$4: D201.C, R205.1, U201.1
MAIN_PROCESSING_UNIT:N$6: C211.1, U201.4, X202.P$1
MAIN_PROCESSING_UNIT:N$9: C213.1, U201.6, X201.P$2
MAIN_PROCESSING_UNIT:N$11: R203.1, R204.2, U201.27
MAIN_PROCESSING_UNIT:N$12: C210.1, R205.2
MPU_DFU: R202.2, S2.2, U201.60
MPU_RX: JP601.6, U201.17
MPU_SCL: JP603.3, U201.58
MPU_SDA: JP603.4, U201.59
MPU_ST_LED0: R8.1, U201.26
MPU_ST_LED1: R8.2, U201.25
MPU_ST_LED2: R8.3, U201.24
MPU_ST_LED3: R8.4, U201.23
MPU_SWCLK: JP601.1, U201.49
MPU_SWDIO: JP601.3, U201.46
MPU_TX: JP601.4, U201.16
unnamed: LED1.A, R8.8
unnamed: LED2.A, R8.7
unnamed: LED3.A, R8.6
unnamed: LED4.A, R8.5
unnamed: J1.8, R2.1
unnamed: J1.1, R2.4
unnamed: C6.1, D2.A, IC1.1, IC1.2, L2.2
unnamed: LED5.A, R10.2
unnamed: Q1.1, R13.2
unnamed: C4.1, CN1.VBUS, L1.2
unnamed: IC101.2, R6.2, S3.3
unnamed: LED6.A, R12.2
unnamed: C11.2, IC2.5
unnamed: D3.A, LS1.1, Q1.3
unnamed: R9.4, U201.34
unnamed: C7.1, C101.1, IC101.6, L2.1
unnamed: R7.8, U201.51
unnamed: R7.6, U201.53
unnamed: IC2.4, JP2.3, JP2.4, R14.2
unnamed: IC503.3, J401.1
unnamed: R7.7, U201.52
unnamed: R9.2, U201.36
unnamed: R9.3, U201.35
unnamed: R9.1, U201.41
unnamed: R11.1, U301.28
unnamed: R11.2, U301.27
unnamed: R11.3, U301.26
unnamed: R11.4, U301.25
unnamed: CN1.ID, R1.1
POWER_LED_OUT: IC2.6, JP2.1, JP2.2
POWER_UNIT:N$2: IC101.3, R101.2, R102.1
POWER_UNIT:N$3: IC101.4, R103.1
POWER_UNIT:N$4: C106.1, IC102.3
POWER_UNIT:N$5: LED102.A, R105.2
POWER_UNIT:N$6: C109.1, IC103.3
POWER_UNIT:N$7: C112.1, C113.1, D101.C, L103.2, R106.2
POWER_UNIT:N$8: D101.A, IC104.1, L102.1
POWER_UNIT:N$9: C113.2, IC104.3, R106.1, R107.2
POWER_UNIT:SUP_CH_STAT1: IC101.1, LED101.A, R104.2
SD_SPI_MISO: J1.7, R2.2, R7.2
SD_SPI_MOSI: J1.3, R2.3, R7.3
SD_SPI_SCLK: J1.5, R7.1
SOUND_OUT: R13.1, U201.21
SPC_EOS: IC401.4, U301.2
SPC_SCLK: IC401.2, U301.30
SPC_ST: IC401.3, U301.29
SPECTROMETER_UNIT:N$1: IC401.13, R401.1
SPECTROMETER_UNIT:N$2: IC401.12, R401.2
SPECTROMETER_UNIT:N$3: IC401.11, R401.3
SPECTROMETER_UNIT:N$4: IC401.10, R401.4
SPECTROMETER_UNIT:N$5: J401.6, R401.8
SPECTROMETER_UNIT:N$6: J401.5, R401.7
SPECTROMETER_UNIT:N$7: J401.4, R401.6
SPECTROMETER_UNIT:N$8: J401.3, R401.5
USBC_N: CN1.D-, R5.1
USBC_P: CN1.D+, R4.1
USB_N: R5.2, U201.44
USB_P: R4.2, U201.45
VBAT: C1.1, C2.1, D1.C, D2.C, IC1.5, IC1.8, JP1.1, JP1.2, R203.2
VUSB: C5.1, C102.1, C202.2, IC101.8, L1.1, R101.1, U201.42

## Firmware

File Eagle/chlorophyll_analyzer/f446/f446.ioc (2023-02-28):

#MicroXplorer Configuration settings - do not modify
ADC1.Channel-0\#ChannelRegularConversion=ADC_CHANNEL_9
ADC1.IPParameters=Rank-0\#ChannelRegularConversion,master,Channel-0\#ChannelRegularConversion,SamplingTime-0\#ChannelRegularConversion,NbrOfConversionFlag
ADC1.NbrOfConversionFlag=1
ADC1.Rank-0\#ChannelRegularConversion=1
ADC1.SamplingTime-0\#ChannelRegularConversion=ADC_SAMPLETIME_3CYCLES
ADC1.master=1
File.Version=6
KeepUserPlacement=false
Mcu.Family=STM32F4
Mcu.IP0=ADC1
Mcu.IP1=DAC
Mcu.IP2=I2C1
Mcu.IP3=NVIC
Mcu.IP4=RCC
Mcu.IP5=SYS
Mcu.IPNb=6
Mcu.Name=STM32F446R(C-E)Tx
Mcu.Package=LQFP64
Mcu.Pin0=PC14-OSC32_IN
Mcu.Pin1=PC15-OSC32_OUT
Mcu.Pin10=PA2
Mcu.Pin11=PA3
Mcu.Pin12=PA4
Mcu.Pin13=PA5
Mcu.Pin14=PA7
Mcu.Pin15=PC4
Mcu.Pin16=PC5
Mcu.Pin17=PB0
Mcu.Pin18=PB1
Mcu.Pin19=PB13
Mcu.Pin2=PH0-OSC_IN
Mcu.Pin20=PB14
Mcu.Pin21=PB15
Mcu.Pin22=PC6
Mcu.Pin23=PC7
Mcu.Pin24=PC9
Mcu.Pin25=PA8
Mcu.Pin26=PA9
Mcu.Pin27=PA11
Mcu.Pin28=PA12
Mcu.Pin29=PA13
Mcu.Pin3=PH1-OSC_OUT
Mcu.Pin30=PA14
Mcu.Pin31=PA15
Mcu.Pin32=PC10
Mcu.Pin33=PC11
Mcu.Pin34=PC12
Mcu.Pin35=PD2
Mcu.Pin36=PB3
Mcu.Pin37=PB4
Mcu.Pin38=PB5
Mcu.Pin39=PB6
Mcu.Pin4=PC0
Mcu.Pin40=PB7
Mcu.Pin41=PB8
Mcu.Pin42=PB9
Mcu.Pin43=VP_SYS_VS_Systick
Mcu.Pin5=PC1
Mcu.Pin6=PC2
Mcu.Pin7=PC3
Mcu.Pin8=PA0-WKUP
Mcu.Pin9=PA1
Mcu.PinsNb=44
Mcu.ThirdPartyNb=0
Mcu.UserConstants=
Mcu.UserName=STM32F446RETx
MxCube.Version=5.3.0
MxDb.Version=DB.5.0.30
NVIC.BusFault_IRQn=true\:0\:0\:false\:false\:true\:false\:false
NVIC.DebugMonitor_IRQn=true\:0\:0\:false\:false\:true\:false\:false
NVIC.HardFault_IRQn=true\:0\:0\:false\:false\:true\:false\:false
NVIC.MemoryManagement_IRQn=true\:0\:0\:false\:false\:true\:false\:false
NVIC.NonMaskableInt_IRQn=true\:0\:0\:false\:false\:true\:false\:false
NVIC.PendSV_IRQn=true\:0\:0\:false\:false\:true\:false\:false
NVIC.PriorityGroup=NVIC_PRIORITYGROUP_4
NVIC.SVCall_IRQn=true\:0\:0\:false\:false\:true\:false\:false
NVIC.SysTick_IRQn=true\:0\:0\:false\:false\:true\:false\:true
NVIC.UsageFault_IRQn=true\:0\:0\:false\:false\:true\:false\:false
PA0-WKUP.GPIOParameters=GPIO_Label
PA0-WKUP.GPIO_Label=EXT_GPIO10
PA0-WKUP.Locked=true
PA0-WKUP.Signal=GPIO_Output
PA1.GPIOParameters=GPIO_Label
PA1.GPIO_Label=EXT_GPIO11
PA1.Locked=true
PA1.Signal=GPIO_Output
PA11.Locked=true
PA11.Signal=USB_OTG_FS_DM
PA12.Locked=true
PA12.Signal=USB_OTG_FS_DP
PA13.Locked=true
PA13.Signal=SYS_JTMS-SWDIO
PA14.Locked=true
PA14.Signal=SYS_JTCK-SWCLK
PA15.GPIOParameters=GPIO_Label
PA15.GPIO_Label=SPI3_CS
PA15.Locked=true
PA15.Signal=GPIO_Output
PA2.Locked=true
PA2.Signal=USART2_TX
PA3.Locked=true
PA3.Signal=USART2_RX
PA4.Locked=true
PA4.Signal=COMP_DAC1_group
PA5.Locked=true
PA5.Signal=COMP_DAC2_group
PA7.GPIOParameters=GPIO_Label
PA7.GPIO_Label=INT_GPIO3
PA7.Locked=true
PA7.Signal=GPIO_Output
PA8.Locked=true
PA8.Mode=Clock-out-1
PA8.Signal=RCC_MCO_1
PA9.Locked=true
PA9.Signal=USB_OTG_FS_VBUS
PB0.GPIOParameters=GPIO_Label
PB0.GPIO_Label=INT_GPIO0
PB0.Locked=true
PB0.Signal=GPIO_Output
PB1.Locked=true
PB1.Signal=ADCx_IN9
PB13.Locked=true
PB13.Signal=SPI2_SCK
PB14.Locked=true
PB14.Signal=SPI2_MISO
PB15.Locked=true
PB15.Signal=SPI2_MOSI
PB3.GPIOParameters=GPIO_Label
PB3.GPIO_Label=EXT_GPIO1
PB3.Locked=true
PB3.Signal=GPIO_Output
PB4.GPIOParameters=GPIO_Label
PB4.GPIO_Label=EXT_GPIO2
PB4.Locked=true
PB4.Signal=GPIO_Output
PB5.GPIOParameters=GPIO_Label
PB5.GPIO_Label=EXT_GPIO3
PB5.Locked=true
PB5.Signal=GPIO_Output
PB6.Mode=I2C
PB6.Signal=I2C1_SCL
PB7.Mode=I2C
PB7.Signal=I2C1_SDA
PB8.GPIOParameters=GPIO_Label
PB8.GPIO_Label=EXT_GPIO4
PB8.Locked=true
PB8.Signal=GPIO_Output
PB9.GPIOParameters=GPIO_Label
PB9.GPIO_Label=EXT_GPIO5
PB9.Locked=true
PB9.Signal=GPIO_Output
PC0.GPIOParameters=GPIO_Label
PC0.GPIO_Label=EXT_GPIO6
PC0.Locked=true
PC0.Signal=GPIO_Output
PC1.GPIOParameters=GPIO_Label
PC1.GPIO_Label=EXT_GPIO7
PC1.Locked=true
PC1.Signal=GPIO_Output
PC10.Locked=true
PC10.Signal=SPI3_SCK
PC11.Locked=true
PC11.Signal=SPI3_MISO
PC12.Locked=true
PC12.Signal=SPI3_MOSI
PC14-OSC32_IN.Locked=true
PC14-OSC32_IN.Signal=RCC_OSC32_IN
PC15-OSC32_OUT.Locked=true
PC15-OSC32_OUT.Signal=RCC_OSC32_OUT
PC2.GPIOParameters=GPIO_Label
PC2.GPIO_Label=EXT_GPI8
PC2.Locked=true
PC2.Signal=GPIO_Output
PC3.GPIOParameters=GPIO_Label
PC3.GPIO_Label=EXT_GPIO9
PC3.Locked=true
PC3.Signal=GPIO_Output
PC4.GPIOParameters=GPIO_Label
PC4.GPIO_Label=INT_GPIO2
PC4.Locked=true
PC4.Signal=GPIO_Output
PC5.GPIOParameters=GPIO_Label
PC5.GPIO_Label=INT_GPIO1
PC5.Locked=true
PC5.Signal=GPIO_Output
PC6.GPIOParameters=GPIO_Label
PC6.GPIO_Label=SPI2_BUSY
PC6.Locked=true
PC6.Signal=GPIO_Input
PC7.GPIOParameters=GPIO_Label
PC7.GPIO_Label=SPI2_CS
PC7.Signal=GPIO_Output
PC9.Locked=true
PC9.Mode=Clock-out-2
PC9.Signal=RCC_MCO_2
PCC.Checker=false
PCC.Line=STM32F446
PCC.MCU=STM32F446R(C-E)Tx
PCC.PartNumber=STM32F446RETx
PCC.Seq0=0
PCC.Series=STM32F4
PCC.Temperature=25
PCC.Vdd=3.3
PD2.GPIOParameters=GPIO_Label
PD2.GPIO_Label=EXT_GPIO0
PD2.Locked=true
PD2.Signal=GPIO_Output
PH0-OSC_IN.Locked=true
PH0-OSC_IN.Signal=RCC_OSC_IN
PH1-OSC_OUT.Locked=true
PH1-OSC_OUT.Signal=RCC_OSC_OUT
PinOutPanel.RotationAngle=270
ProjectManager.AskForMigrate=true
ProjectManager.BackupPrevious=false
ProjectManager.CompilerOptimize=6
ProjectManager.ComputerToolchain=false
ProjectManager.CoupleFile=false
ProjectManager.CustomerFirmwarePackage=
ProjectManager.DefaultFWLocation=true
ProjectManager.DeletePrevious=true
ProjectManager.DeviceId=STM32F446RETx
ProjectManager.FirmwarePackage=STM32Cube FW_F4 V1.24.1
ProjectManager.FreePins=false
ProjectManager.HalAssertFull=false
ProjectManager.HeapSize=0x200
ProjectManager.KeepUserCode=true
ProjectManager.LastFirmware=true
ProjectManager.LibraryCopy=0
ProjectManager.MainLocation=Src
ProjectManager.NoMain=false
ProjectManager.PreviousToolchain=
ProjectManager.ProjectBuild=false
ProjectManager.ProjectFileName=f446.ioc
ProjectManager.ProjectName=f446
ProjectManager.StackSize=0x400
ProjectManager.TargetToolchain=EWARM V8
ProjectManager.ToolChainLocation=
ProjectManager.UnderRoot=false
ProjectManager.functionlistsort=
RCC.CECFreq_Value=32786.88524590164
RCC.CortexFreq_Value=16000000
RCC.FamilyName=M
RCC.IPParameters=CECFreq_Value,CortexFreq_Value,FamilyName,PLLCLKFreq_Value,PLLI2SPCLKFreq_Value,PLLI2SQCLKFreq_Value,PLLI2SRCLKFreq_Value,PLLQCLKFreq_Value,PLLRCLKFreq_Value,PLLSAIPCLKFreq_Value,PLLSAIQCLKFreq_Value,SAIAFreq_Value,SAIBFreq_Value,SDIOFreq_Value,USBFreq_Value,VCOI2SInputFreq_Value,VCOI2SOutputFreq_Value,VCOInputFreq_Value,VCOOutputFreq_Value,VCOSAIInputFreq_Value,VCOSAIOutputFreq_Value
RCC.PLLCLKFreq_Value=96000000
RCC.PLLI2SPCLKFreq_Value=96000000
RCC.PLLI2SQCLKFreq_Value=96000000
RCC.PLLI2SRCLKFreq_Value=96000000
RCC.PLLQCLKFreq_Value=96000000
RCC.PLLRCLKFreq_Value=96000000
RCC.PLLSAIPCLKFreq_Value=96000000
RCC.PLLSAIQCLKFreq_Value=96000000
RCC.SAIAFreq_Value=96000000
RCC.SAIBFreq_Value=96000000
RCC.SDIOFreq_Value=96000000
RCC.USBFreq_Value=96000000
RCC.VCOI2SInputFreq_Value=1000000
RCC.VCOI2SOutputFreq_Value=192000000
RCC.VCOInputFreq_Value=1000000
RCC.VCOOutputFreq_Value=192000000
RCC.VCOSAIInputFreq_Value=1000000
RCC.VCOSAIOutputFreq_Value=192000000
SH.ADCx_IN9.0=ADC1_IN9,IN9
SH.ADCx_IN9.ConfNb=1
SH.COMP_DAC1_group.0=DAC_OUT1,DAC_OUT1
SH.COMP_DAC1_group.ConfNb=1
SH.COMP_DAC2_group.0=DAC_OUT2,DAC_OUT2
SH.COMP_DAC2_group.ConfNb=1
VP_SYS_VS_Systick.Mode=SysTick
VP_SYS_VS_Systick.Signal=SYS_VS_Systick
board=custom

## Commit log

2023-02-28 ハードウェア設計ファイルを追加
    [block_diagram.sch, chlorophyll_analizer_extra.brd, chlorophyll_analizer_extra.f3d, chlorophyll_analizer_extra.sch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]
2023-03-02 不要ファイルを削除
2023-03-02 Update README.md
    デモを追加
2023-03-14 文章修正

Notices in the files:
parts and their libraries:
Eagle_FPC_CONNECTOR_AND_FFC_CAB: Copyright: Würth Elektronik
